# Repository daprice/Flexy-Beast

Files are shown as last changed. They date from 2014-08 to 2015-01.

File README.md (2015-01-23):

Flexy Beast
===========

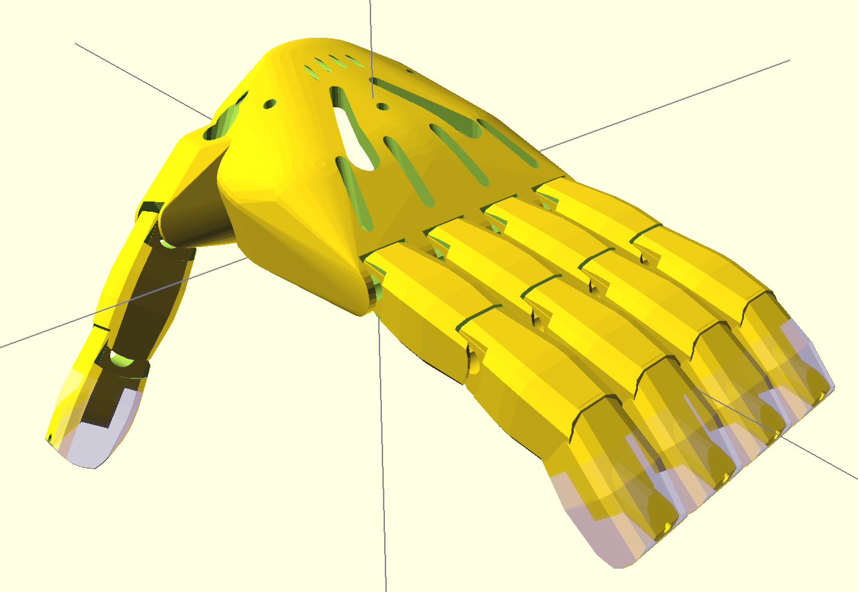
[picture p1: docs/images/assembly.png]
Screenshot of Flexy Beast hand in OpenSCAD


The Flexy Beast is a wrist-powered prosthetic hand for the [e-NABLE Project](http://enablingthefuture.org). This is a mashup of the [Parametric Cyborg Beast](http://www.thingiverse.com/thing:320173) by MakerBlock and the [Flexy Hand](http://www.thingiverse.com/thing:380665) by Steve Wood/Gyrobot. Like the Flexy-Hand, the Flexy Beast uses flexible joints to replace the Chicago screws and elastics used on previous e-NABLE designs. This makes the hand lightweight, less expensive, better looking, more adaptable for smaller sizes, and easier to assemble and use.

I recommend using Filaflex (get these from the original [Flexy Hand](http://www.thingiverse.com/thing:380665)) or [molded silicone flex joints](https://github.com/daprice/Flexy-Joint/tree/FlexyBeast) for this design. See the [Flexy Joint wiki](https://github.com/daprice/Flexy-Joint/wiki) for information about materials to use and the process of making these joints.

### Finger Pads
The Flexy Beast fingers can be made with silicone finger pads for improved grip. These finger pads are designed to be easily removeable and replaceable by hand, but attach firmly enough to stay on during use.
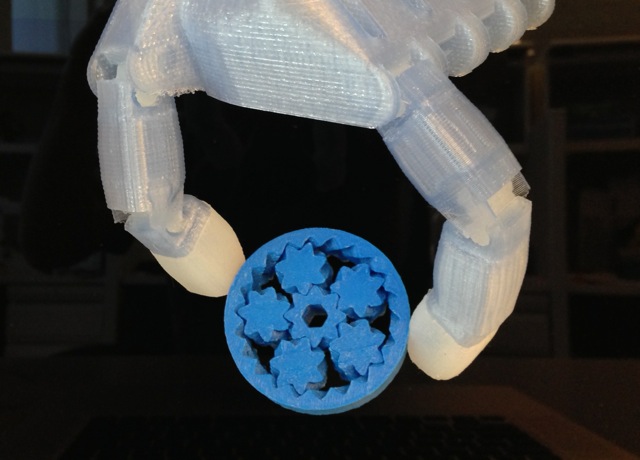
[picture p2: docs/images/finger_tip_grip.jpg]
Fingertips with the ends covered in silicone padding


## Hand Assembly
See the [ThingDoc documentation for the Flexy Beast](http://daprice.github.io/Flexy-Beast) for detailed sizing and assembly instructions.

## Future Improvements
* Flexible joints for gauntlet attachment (this is currently unchanged from the original Cyborg Beast)
* Possible aesthetic options such as text, decorative elements, superhero themes, etc.

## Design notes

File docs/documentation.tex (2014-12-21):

\documentclass[11pt]{article}
\usepackage[latin2]{inputenc}
\usepackage{a4wide}
\usepackage{graphicx}
\usepackage{hyperref}
\hypersetup{colorlinks=true,linkcolor=blue}
\title{Flexy Beast Documentation}
\author{ThingDoc}

\begin{document}

\maketitle
\begin{center}
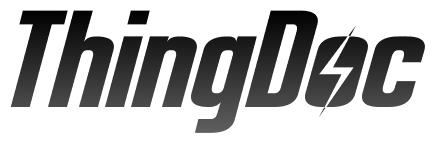
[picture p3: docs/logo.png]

\end{center}
The Flexy Beast is a wrist-powered prosthetic hand for the e-NABLE Project. This is a mashup of the Parametric Cyborg Beast by MakerBlock and the Flexy Hand by Steve Wood/Gyrobot. Like the Flexy-Hand, the Flexy Beast uses flexible joints to replace the Chicago screws and elastics used on previous e-NABLE designs. This makes the hand lightweight, less expensive, better looking, more adaptable for smaller sizes, and easier to assemble and use.

\newpage

\tableofcontents

\newpage

\section{Bill of Materials}
List of things you need to build the machine divided by categories.

\subsection{Prerequisites!}
\begin{itemize}
\item 1x \hyperlink{thing_config\_file}{Configuration File}
\end{itemize}

\subsection{Flexible}
\begin{itemize}
\item 10x \hyperlink{thing_flexy\_joint}{Flexy Joint}
\end{itemize}

\subsection{Other}
\begin{itemize}
\item 5x \hyperlink{thing_string}{String}
\end{itemize}

\subsection{Printed}
\begin{itemize}
\item 1x \hyperlink{thing_thumb\_tip}{Thumb Tip}
\item 1x \hyperlink{thing_index\_base}{Index Finger Base}
\item 1x \hyperlink{thing_pinky\_tip}{Pinky Finger Tip}
\item 5x \hyperlink{thing_finger\_tip\_mold}{Finger Tip Mold}
\item 1x \hyperlink{thing_pinky\_base}{Pinky Finger Base}
\item 1x \hyperlink{thing_ring\_tip}{Ring Finger Tip}
\item 1x \hyperlink{thing_index\_tip}{Index Finger Tip}
\item 1x \hyperlink{thing_palm}{Palm}
\item 1x \hyperlink{thing_ring\_base}{Ring Finger Base}
\item 1x \hyperlink{thing_thumb\_base}{Thumb Base}
\item 1x \hyperlink{thing_middle\_tip}{Middle Finger Tip}
\item 1x \hyperlink{thing_middle\_base}{Middle Finger Base}
\end{itemize}

\newpage

\section{Things Overview}
List of things and their descriptions.

\hypertarget{thing_middle\_finger\_assembly}{\subsection{Assembled Middle Finger}}

\hypertarget{thing_ring\_finger\_assembly}{\subsection{Assembled Ring Finger}}

\hypertarget{thing_palm}{\subsection{Palm}}
Palm - rendered from parts/palm.scad
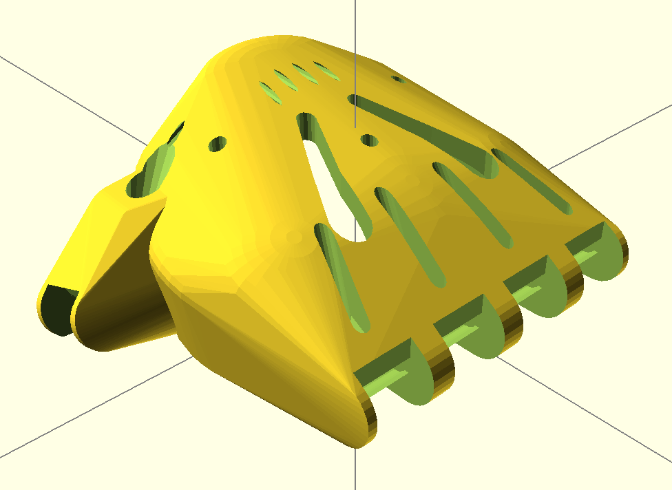
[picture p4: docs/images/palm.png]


\hypertarget{thing_ring\_base}{\subsection{Ring Finger Base}}
Proximal phalanx for ring finger - rendered from parts/finger_ring_base.scad

\hypertarget{thing_finger\_tip\_mold}{\subsection{Finger Tip Mold}}
Mold for casting silicone finger tip grip - rendered from parts/finger_tip_mold.scad


\hypertarget{thing_middle\_tip}{\subsection{Middle Finger Tip}}
Distal phalanx of middle finger - rendered from parts/finger_middle_tip.scad

\hypertarget{thing_ring\_tip}{\subsection{Ring Finger Tip}}
Distal phalanx of ring finger - rendered from parts/finger_ring_tip.scad

\hypertarget{thing_flexy\_joint}{\subsection{Flexy Joint}}
Flex joint - can be molded in silicone or printed in Filaflex. The Configuration File instructions will help you find a good size for these.

\hypertarget{thing_thumb\_base}{\subsection{Thumb Base}}
Proximal phalanx for thumb - rendered from parts/thumb_base.scad

\hypertarget{thing_pinky\_finger\_assembly}{\subsection{Assembled Pinky Finger}}

\hypertarget{thing_config\_file}{\subsection{Configuration File}}
Configuration settings for Flexy Beast, required to generate correctly sized STLs of the printed parts. See the Configuration File Assembly instructions to set this up.

\hypertarget{thing_string}{\subsection{String}}
Just some string

\hypertarget{thing_pinky\_tip}{\subsection{Pinky Finger Tip}}
Distal phalanx of pinky finger - rendered from parts/finger_pinky_tip.scad

\hypertarget{thing_middle\_base}{\subsection{Middle Finger Base}}
Proximal phalanx for middle finger - rendered from parts/finger_middle_base.scad

\hypertarget{thing_thumb\_tip\_grip}{\subsection{Grippy Thumb Tip}}
Molded silicone grippy thumb tip

\hypertarget{thing_index\_base}{\subsection{Index Finger Base}}
Proximal phalanx for index finger - rendered from parts/finger_index_base.scad

\hypertarget{thing_finger\_tip\_grip}{\subsection{Grippy Finger Tip}}
The Flexy Beast fingers can be made with silicone finger pads for improved grip. These finger pads are designed to be easily removeable and replaceable by hand, but attach firmly enough to stay on during use. Dragon Skin 10 silicone produces very soft and grippy pads; Dragon Skin 30 is tougher.


\hypertarget{thing_thumb\_tip}{\subsection{Thumb Tip}}
Distal phalanx of thumb - rendered from parts/thumb_tip.scad


\hypertarget{thing_thumb\_assembly}{\subsection{Assembled Thumb}}

\hypertarget{thing_index\_tip}{\subsection{Index Finger Tip}}
Distal phalanx of index finger - rendered from parts/finger_index_tip.scad

\hypertarget{thing_index\_finger\_assembly}{\subsection{Assembled Index Finger}}

\hypertarget{thing_pinky\_base}{\subsection{Pinky Finger Base}}
Proximal phalanx for pinky finger - rendered from parts/finger_pinky_base.scad

\newpage

\section{Assembly Instructions}

\subsection{Assemble Grippy Finger Tip}
Things needed:
\begin{itemize}
\item 1x \hyperlink{thing_finger\_tip\_mold}{Finger Tip Mold}
\end{itemize}
Steps:
\begin{enumerate}
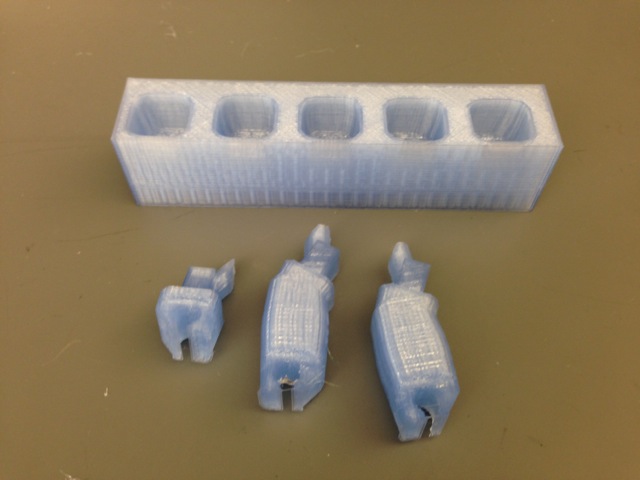
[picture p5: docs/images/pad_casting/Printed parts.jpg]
\item Print the finger tip and mold.\\ 
\item Insert the string through the fingertip and tie off the end prior to molding (not shown in all photos here).\\ 
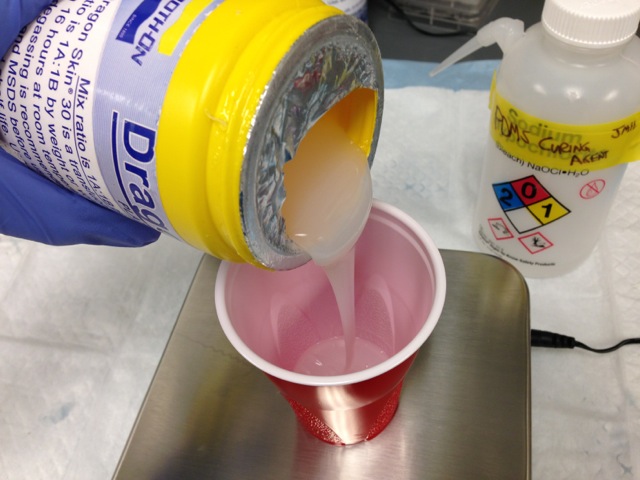
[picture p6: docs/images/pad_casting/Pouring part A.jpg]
\item Mix silicone according to the instructions from the supplier. Wear gloves and follow the supplier's safety instructions while working with liquid silicone.\\ 
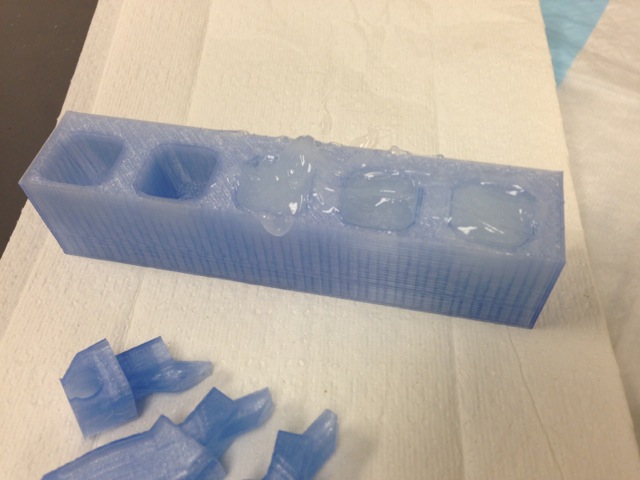
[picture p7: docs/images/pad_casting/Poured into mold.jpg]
\item Pour the liquid silicone to mostly fill the fingertip mold.\\ 
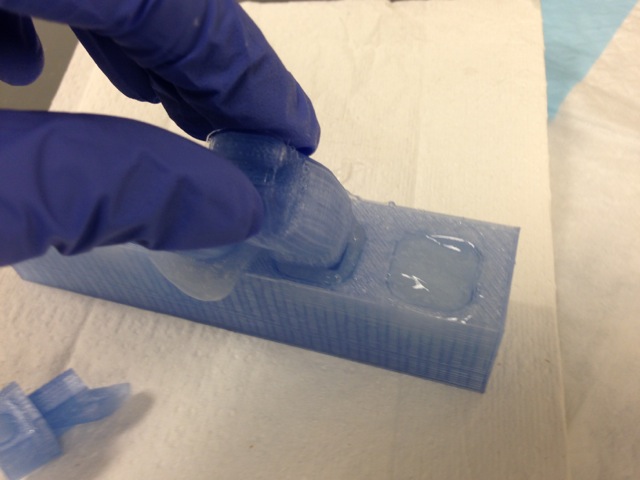
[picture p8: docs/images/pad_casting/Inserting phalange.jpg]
\item Insert the printed fingertip piece into the filled mold.\\ 
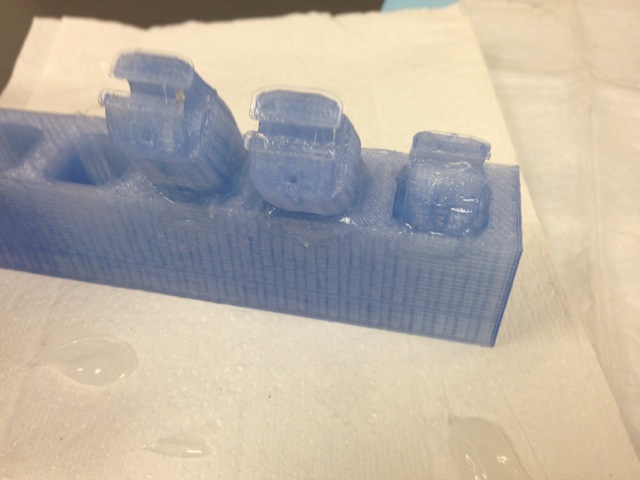
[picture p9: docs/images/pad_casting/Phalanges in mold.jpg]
\item Remove any excess silicone. If necessary, use tape to hold the phalange in place.\\ 
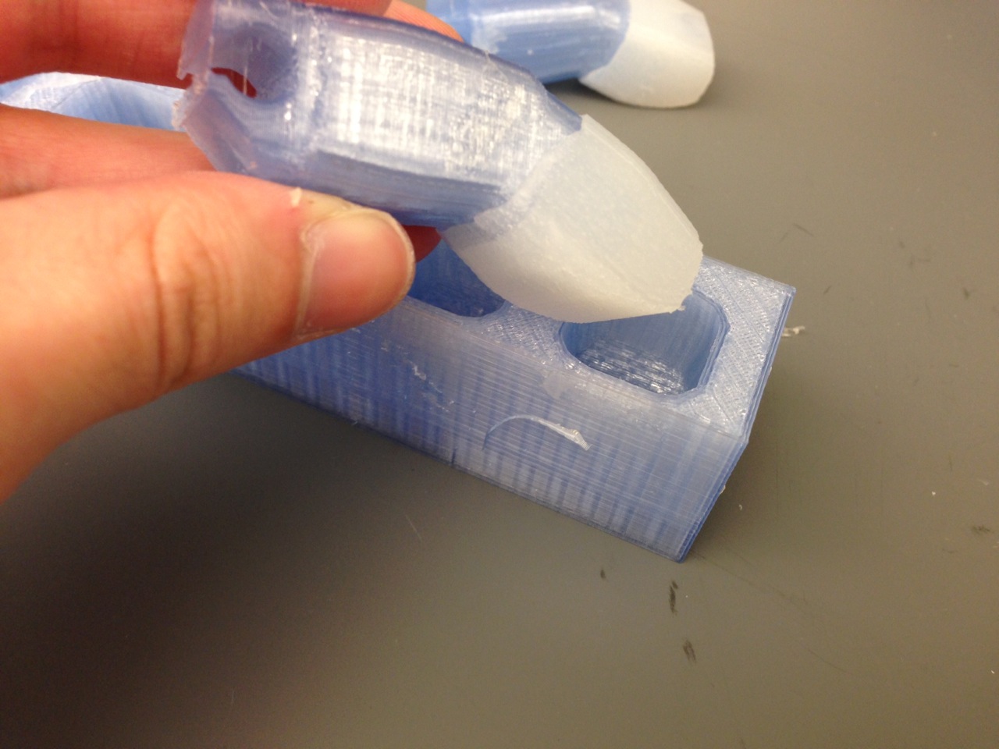
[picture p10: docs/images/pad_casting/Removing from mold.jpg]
\item When the silicone is cured, remove the fingertip and silicone pad from the mold. The pad may stay on the fingertip or it may need to be removed separately.\\ 
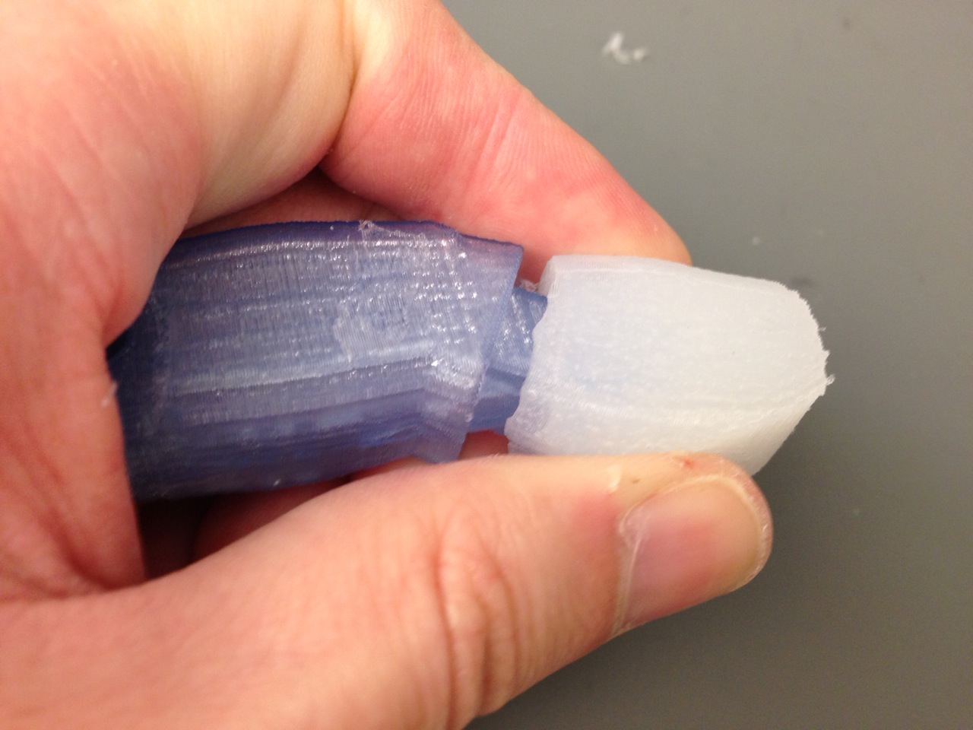
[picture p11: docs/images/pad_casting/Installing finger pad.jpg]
\item If the pad came off the fingertip during demolding, it can be reattached by pushing it over the end of the fingertip.\\ 
\item If necessary, use an x-acto knife to trim off excess silicone so that the edges of the pad are flush with the edges of the fingertip.
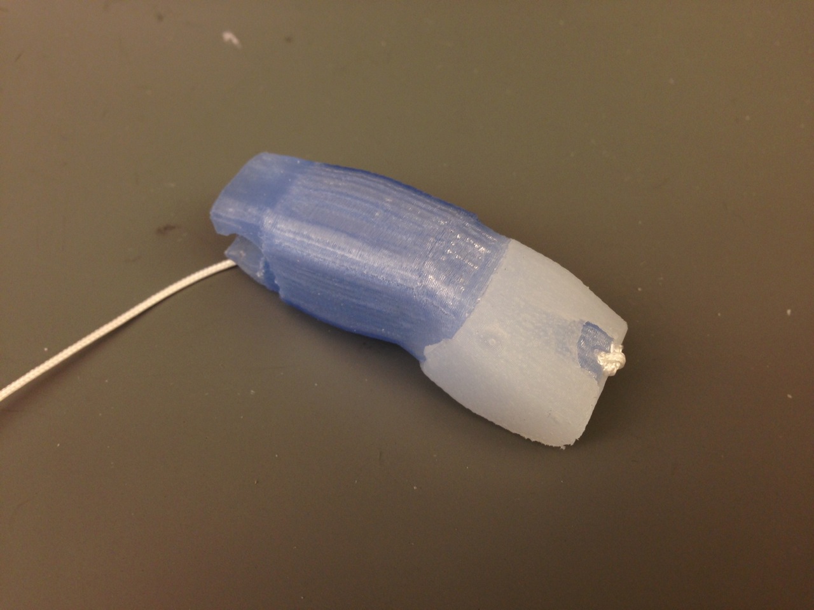
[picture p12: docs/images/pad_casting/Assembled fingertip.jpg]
\item The fingertip pads are finished. Continue installing them onto the hand.\\ 
\end{enumerate}

\subsection{Assemble Grippy Finger Tip}
Things needed:
\begin{itemize}
\item 1x \hyperlink{thing_finger\_tip\_mold}{Finger Tip Mold}
\end{itemize}
Steps:
\begin{enumerate}
\item Print the finger tip and mold.\\ 
\item Insert the string through the fingertip and tie off the end prior to molding (not shown in all photos here).\\ 
\item Mix silicone according to the instructions from the supplier. Wear gloves and follow the supplier's safety instructions while working with liquid silicone.\\ 
\item Pour the liquid silicone to mostly fill the fingertip mold.\\ 
\item Insert the printed fingertip piece into the filled mold.\\ 
\item Remove any excess silicone. If necessary, use tape to hold the phalange in place.\\ 
\item When the silicone is cured, remove the fingertip and silicone pad from the mold. The pad may stay on the fingertip or it may need to be removed separately.\\ 
\item If the pad came off the fingertip during demolding, it can be reattached by pushing it over the end of the fingertip.\\ 
\item If necessary, use an x-acto knife to trim off excess silicone so that the edges of the pad are flush with the edges of the fingertip.
\item The fingertip pads are finished. Continue installing them onto the hand.\\ 
\end{enumerate}

\subsection{Assemble Configuration File}Steps:
\begin{enumerate}
\item Open config.scad in your favorite text editor.
\item As per the normal Cyborg Beast instructions, measure the width of the knuckles in the non-affected hand and convert to millimeters.
\item Add 5 to that result and then divide by 55.
\item Replace the x-, y-, and zScaleFactor variables in config.scad with that number.
\item If desired, adjust the proportions of the hand by changing those variables individually. xScaleFactor controls the width of the hand, yScaleFactor controls the length, and zScaleFactor controls the height.
\item Open assembly.scad in OpenSCAD to check that the flexy joint holes are not too large for the hand (should only be necessary for small children). If necessary, reduce the jointDia and jointThick variables. jointDia=5 and jointThick=2 is a good amount for smaller hands.
\item Set the fingerPads variable to true or false depending on whether you want to cast silicone finger pads for improved grip.
\item Open palm.scad, finger\_base.scad, finger\_tip.scad, and thumb\_tip.scad in OpenSCAD, render each part (F6), and export as STL, then print. Suggested print settings are 0.2mm or smaller layer height, 3 perimeters, and 25\% rectilinear or hexagonal infill.
\end{enumerate}

\subsection{Assemble Grippy Finger Tip}
Things needed:
\begin{itemize}
\item 1x \hyperlink{thing_finger\_tip\_mold}{Finger Tip Mold}
\end{itemize}
Steps:
\begin{enumerate}
\item Print the finger tip and mold.\\ 
\item Insert the string through the fingertip and tie off the end prior to molding (not shown in all photos here).\\ 
\item Mix silicone according to the instructions from the supplier. Wear gloves and follow the supplier's safety instructions while working with liquid silicone.\\ 
\item Pour the liquid silicone to mostly fill the fingertip mold.\\ 
\item Insert the printed fingertip piece into the filled mold.\\ 
\item Remove any excess silicone. If necessary, use tape to hold the phalange in place.\\ 
\item When the silicone is cured, remove the fingertip and silicone pad from the mold. The pad may stay on the fingertip or it may need to be removed separately.\\ 
\item If the pad came off the fingertip during demolding, it can be reattached by pushing it over the end of the fingertip.\\ 
\item If necessary, use an x-acto knife to trim off excess silicone so that the edges of the pad are flush with the edges of the fingertip.
\item The fingertip pads are finished. Continue installing them onto the hand.\\ 
\end{enumerate}

\subsection{Assemble Grippy Finger Tip}
Things needed:
\begin{itemize}
\item 1x \hyperlink{thing_finger\_tip\_mold}{Finger Tip Mold}
\end{itemize}
Steps:
\begin{enumerate}
\item Print the finger tip and mold.\\ 
\item Insert the string through the fingertip and tie off the end prior to molding (not shown in all photos here).\\ 
\item Mix silicone according to the instructions from the supplier. Wear gloves and follow the supplier's safety instructions while working with liquid silicone.\\ 
\item Pour the liquid silicone to mostly fill the fingertip mold.\\ 
\item Insert the printed fingertip piece into the filled mold.\\ 
\item Remove any excess silicone. If necessary, use tape to hold the phalange in place.\\ 
\item When the silicone is cured, remove the fingertip and silicone pad from the mold. The pad may stay on the fingertip or it may need to be removed separately.\\ 
\item If the pad came off the fingertip during demolding, it can be reattached by pushing it over the end of the fingertip.\\ 
\item If necessary, use an x-acto knife to trim off excess silicone so that the edges of the pad are flush with the edges of the fingertip.
\item The fingertip pads are finished. Continue installing them onto the hand.\\ 
\end{enumerate}

\subsection{Assemble Flexy Beast}
Things needed:
\begin{itemize}
\item 1x \hyperlink{thing_middle\_finger\_assembly}{Assembled Middle Finger}
\item 1x \hyperlink{thing_pinky\_finger\_assembly}{Assembled Pinky Finger}
\item 1x \hyperlink{thing_config\_file}{Configuration File}
\item 1x \hyperlink{thing_thumb\_assembly}{Assembled Thumb}
\item 1x \hyperlink{thing_ring\_finger\_assembly}{Assembled Ring Finger}
\item 1x \hyperlink{thing_palm}{Palm}
\item 1x \hyperlink{thing_index\_finger\_assembly}{Assembled Index Finger}
\end{itemize}
Steps:
\begin{enumerate}
\item Print the palm, thumb base, thumb tip, and four each of the finger base and tip. These can be scaled as needed in each dimension using the x-, y-, and zScaleFactor variables in the OpenSCAD code.
\item Insert a string through each fingertip (the hole may need to be drilled slightly to deburr) and tie it off on the end.\\ 
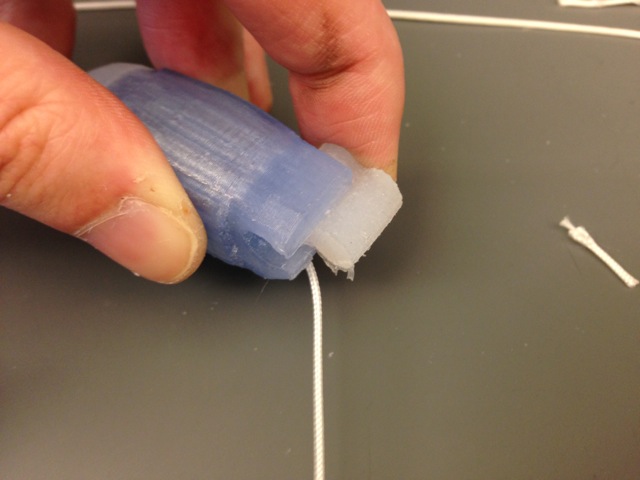
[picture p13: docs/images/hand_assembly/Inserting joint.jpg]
\item After making the 3D printed parts and flexible joints, slide a flex joint into the proximal end of each finger.\\ 
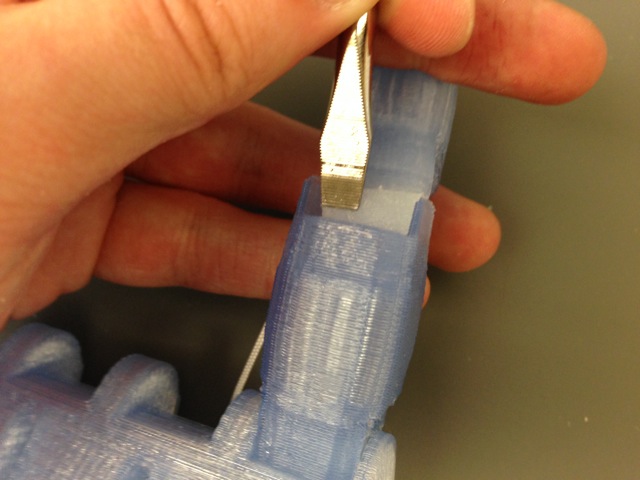
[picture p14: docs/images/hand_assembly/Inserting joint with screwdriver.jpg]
\item Use a flat screwdriver or other thin, flat tool to insert the other end of the joint into the corresponding slot on the next inner segment.\\ 
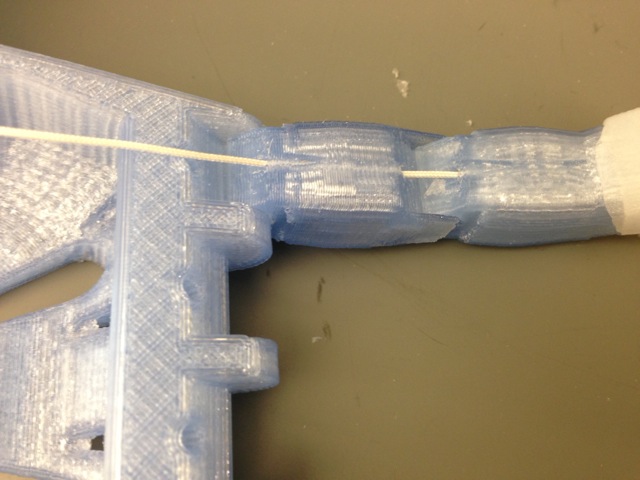
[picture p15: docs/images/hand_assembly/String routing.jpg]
\item Route the string through all the finger segments.\\ 
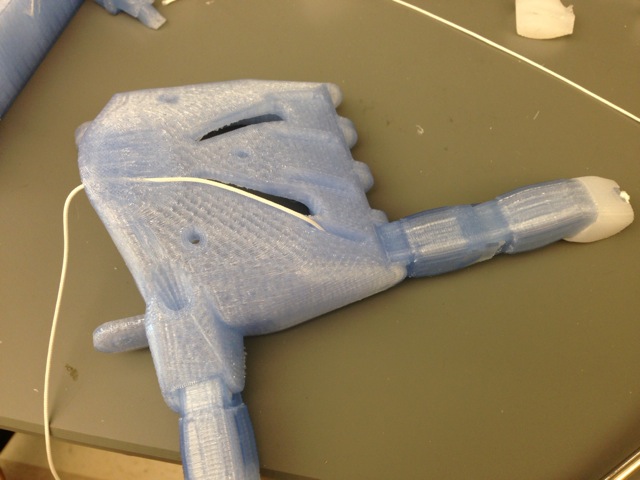
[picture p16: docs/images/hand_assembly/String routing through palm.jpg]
\item Route the string through the palm.\\ 
\end{enumerate}

\newpage

\end{document}

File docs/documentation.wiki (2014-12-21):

== Bill of Materials ==

=== Prerequisites! ===
{| class="wikitable sortable" border="1"
|-
! scope="col" | Quantity
! scope="col" | Description
! scope="col" | Type
! scope="col" class="unsortable" | Comments
! scope="col" class="unsortable" | Diagram
|-
| 1 || Configuration File ||  ||  ||
|}

=== Flexible ===
{| class="wikitable sortable" border="1"
|-
! scope="col" | Quantity
! scope="col" | Description
! scope="col" | Type
! scope="col" class="unsortable" | Comments
! scope="col" class="unsortable" | Diagram
|-
| 10 || Flexy Joint ||  ||  ||
|}

=== Other ===
{| class="wikitable sortable" border="1"
|-
! scope="col" | Quantity
! scope="col" | Description
! scope="col" | Type
! scope="col" class="unsortable" | Comments
! scope="col" class="unsortable" | Diagram
|-
| 5 || String ||  ||  ||
|}

=== Printed ===
{| class="wikitable sortable" border="1"
|-
! scope="col" | Quantity
! scope="col" | Description
! scope="col" | Type
! scope="col" class="unsortable" | Comments
! scope="col" class="unsortable" | Diagram
|-
| 1 || Thumb Tip ||  ||  || 50px
|-
| 1 || Index Finger Base ||  ||  ||
|-
| 1 || Pinky Finger Tip ||  ||  ||
|-
| 5 || Finger Tip Mold ||  ||  || 50px
|-
| 1 || Pinky Finger Base ||  ||  ||
|-
| 1 || Ring Finger Tip ||  ||  ||
|-
| 1 || Index Finger Tip ||  ||  ||
|-
| 1 || Palm ||  ||  || 50px
|-
| 1 || Ring Finger Base ||  ||  ||
|-
| 1 || Thumb Base ||  ||  ||
|-
| 1 || Middle Finger Tip ||  ||  ||
|-
| 1 || Middle Finger Base ||  ||  ||
|}

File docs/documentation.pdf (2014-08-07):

## Flexy Beast Documentation

ThingDoc

August 7, 2014

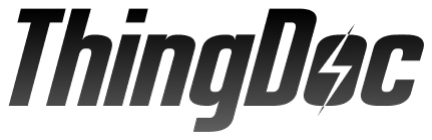
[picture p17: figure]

The Flexy Beast is a wrist-powered prosthetic hand for the e-NABLE Project. This is a mashup of the Parametric Cyborg Beast by MakerBlock and the Flexy Hand by Steve Wood/Gyrobot. Like the Flexy-Hand, the Flexy Beast uses flexible joints to replace the Chicago screws and elastics used on previous e-NABLE designs. This makes the hand lightweight, less expensive, better looking, more adaptable for smaller sizes, and easier to assemble and use.

## Contents

1 Bill of Materials | 3
1.1 Prerequisites! | | 3
1.2 Flexible | | 3
1.3 Other | | 3
1.4 Printed | | 3
2 Things Overview | 4
2.1 Grippy Thumb Tip | | 4
2.2 Configuration File | | 4
2.3 String | | 4
2.4 Grippy Finger Tip | | 4
2.5 Finger Tip | | 4
2.6 Finger Base | | 5
2.7 Thumb Tip | | 5
2.8 Assembled Thumb | | 5
2.9 Palm | | 5
2.10 Flexy Joint | | 5
2.11 Assembled Finger | | 6
2.12 Finger Tip Mold | | 6
3 Assembly Instructions | 7
3.1 Assemble Configuration File | | 7
3.2 Assemble Grippy Finger Tip | | 7
3.3 Assemble Flexy Beast | | 9

## 1 Bill of Materials

List of things you need to build the machine divided by categories.

### 1.1 Prerequisites!

- 1x Configuration File

### 1.2 Flexible

- 10x Flexy Joint

### 1.3 Other

- 5x String

### 1.4 Printed

- 4x Finger Tip
- 5x Finger Tip Mold
- 1x Palm
- 5x Finger Base
- 1x Thumb Tip

## 2 Things Overview

List of things and their descriptions.

### 2.1 Grippy Thumb Tip

Molded silicone grippy thumb tip

### 2.2 Configuration File

Configuration settings for Flexy Beast, required to generate correctly sized STLs of the printed parts. See the Configuration File Assembly instructions to set this up.

### 2.3 String

Just some string

### 2.4 Grippy Finger Tip

The Flexy Beast fingers can be made with silicone finger pads for improved grip. These finger pads are designed to be easily removeable and replaceable by hand, but attach firmly enough to stay on during use. Dragon Skin 10 silicone produces very soft and grippy pads; Dragon

Skin 30 is tougher.


### 2.5 Finger Tip

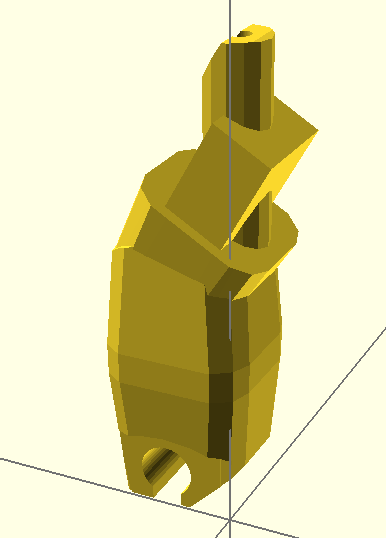
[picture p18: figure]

Distal phalanx of fingers - rendered from parts/finger tip.scad

### 2.6 Finger Base

Proximal phalanx for all digits (fingers and thumb) - rendered from parts/finger base.scad

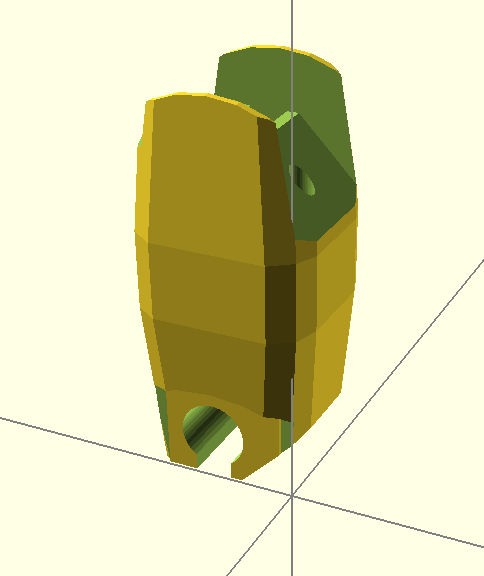
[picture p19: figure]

### 2.7 Thumb Tip

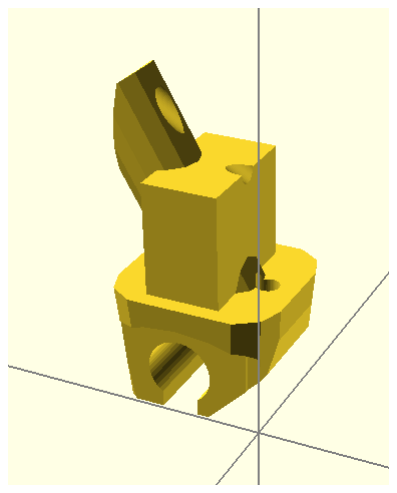
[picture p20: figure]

Distal phalanx of thumb - rendered from parts/thumb tip.scad

### 2.8 Assembled Thumb

### 2.9 Palm

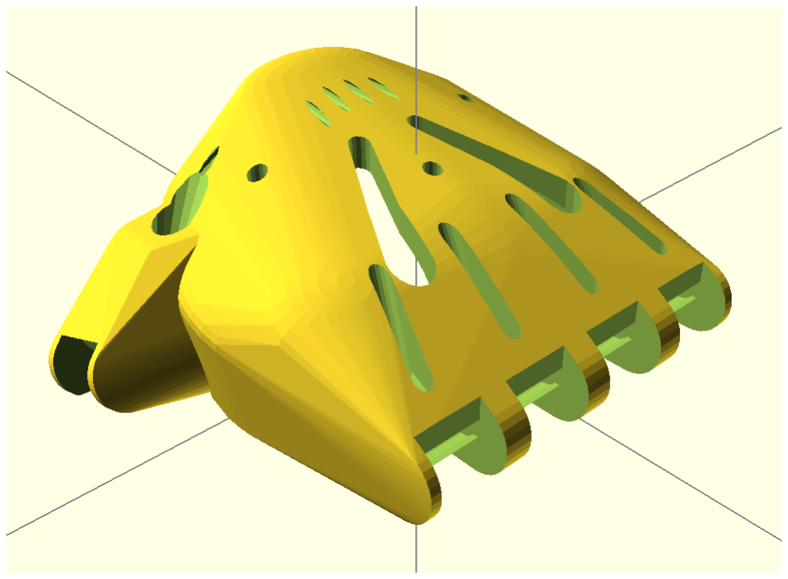
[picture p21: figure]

Palm - rendered from parts/palm.scad

### 2.10 Flexy Joint

Flex joint - can be molded in silicone or printed in Filaflex. The Configuration File instructions will help you find a good size for these.

### 2.11 Assembled Finger

### 2.12 Finger Tip Mold

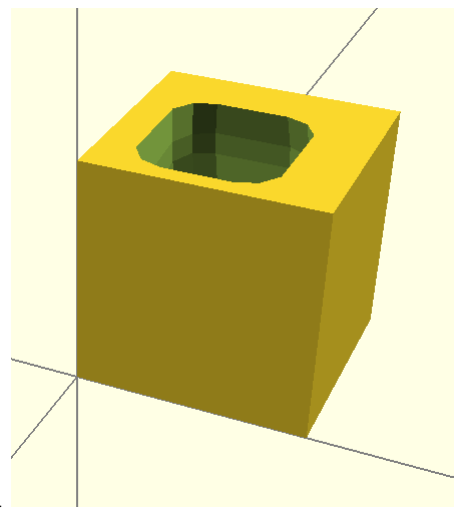
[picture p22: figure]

Mold for casting silicone finger tip grip - rendered from parts/finger tip mold.scad

## 3 Assembly Instructions

### 3.1 Assemble Configuration File

Steps:

1. Open config.scad in your favorite text editor.
2. As per the normal Cyborg Beast instructions, measure the width of the knuckles in the non-affected hand and convert to millimeters.
3. Add 5 to that result and then divide by 55.
4. Replace the x-, y-, and zScaleFactor variables in config.scad with that number.
5. If desired, adjust the proportions of the hand by changing those variables individually. xScaleFactor controls the width of the hand, yScaleFactor controls the length, and zScaleFactor controls the height.
6. Open assembly.scad in OpenSCAD to check that the flexy joint holes are not too large for the hand (should only be necessary for small children). If necessary, reduce the jointDia and jointThick variables. jointDia=5 and jointThick=2 is a good amount for smaller hands.
7. Set the fingerPads variable to true or false depending on whether you want to cast silicone finger pads for improved grip.
8. In palm.scad, finger base.scad, finger tip.scad, and thumb tip.scad, uncomment the first line that renders the part.
9. Render each part (F6) and export as STL, then print.

### 3.2 Assemble Grippy Finger Tip

Things needed:

- 1x Finger Tip
- 1x Finger Tip Mold

Steps:


1. Print the finger tip and mold.

parts.jpg

2. Insert the string through the fingertip and tie off the end prior to molding (not shown in all photos here).

with string.jpg

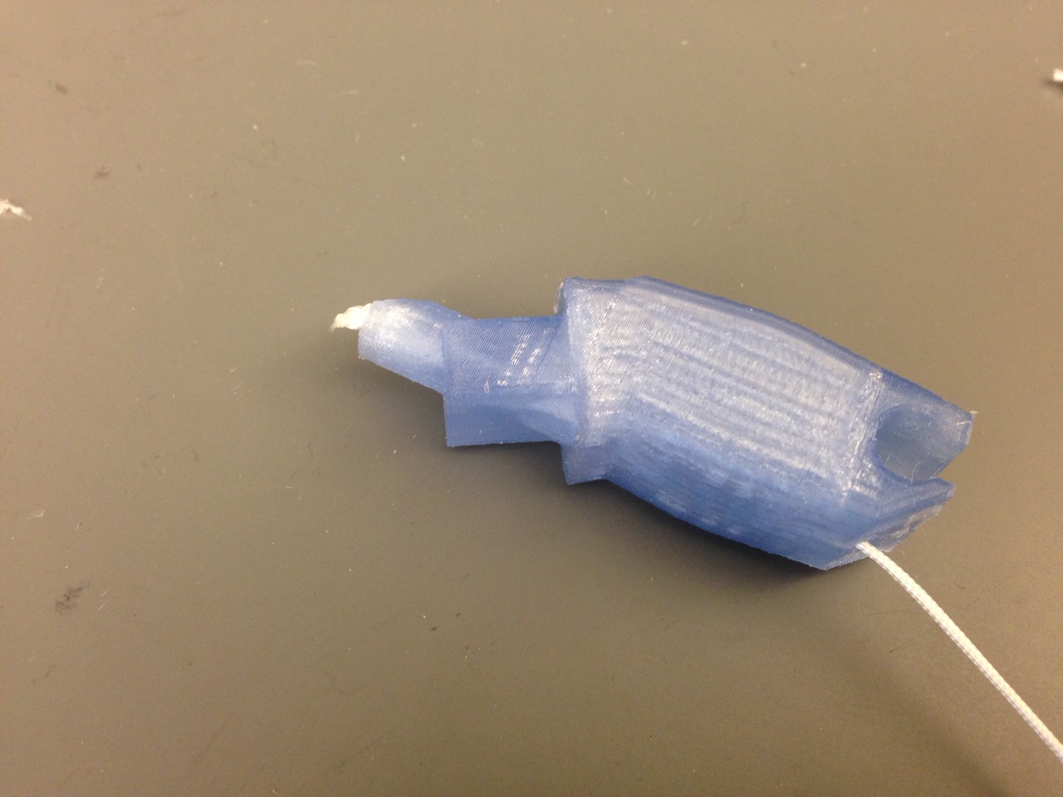
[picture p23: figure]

3. Mix silicone according to the instructions from the supplier. Wear gloves and follow the supplier’s safety instructions while working with liquid silicone.

part A.jpg


4. Pour the liquid silicone to mostly fill the fingertip mold.

into mold.jpg


5. Insert the printed fingertip piece into the filled mold.

phalange.jpg


6. Remove any excess silicone. If necessary, use tape to hold the phalange in place.

in mold.jpg


7. When the silicone is cured, remove the fingertip and silicone pad from the mold. The pad may stay on the fingertip or it may need to be removed separately.

from mold.jpg


8. If the pad came off the fingertip during demolding, it can be reattached by pushing it over the end of the fingertip.

finger pad.jpg


9. If necessary, use an x-acto knife to trim off excess silicone so that the edges of the pad are flush with the edges of the fingertip.
10. The fingertip pads are finished. Continue installing them onto the hand.

fingertip.jpg


### 3.3 Assemble Flexy Beast

Things needed:

- 1x Palm
- 1x Assembled Thumb
- 1x Configuration File
- 4x Assembled Finger

Steps:

1. Print the palm, thumb base, thumb tip, and four each of the finger base and tip. These can be scaled as needed in each dimension using the x-, y-, and zScaleFactor variables in the OpenSCAD code.
2. Insert a string through each fingertip (the hole may need to be drilled slightly to deburr) and tie it off on the end.

with string.jpg

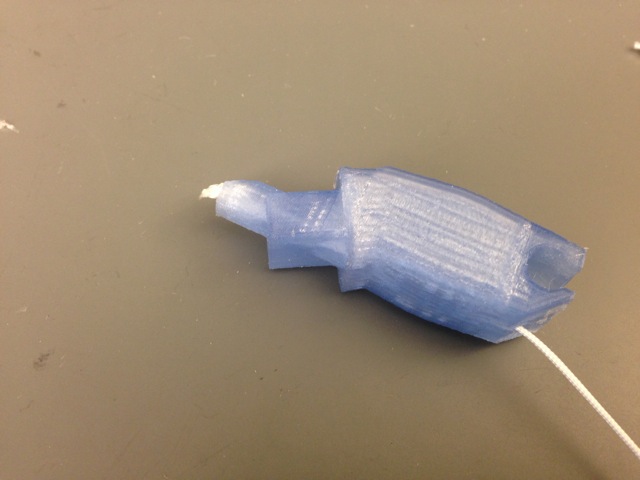
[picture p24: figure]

3. After making the 3D printed parts and flexible joints, slide a flex joint into the proximal end of each finger.

joint.jpg


4. Use a flat screwdriver or other thin, flat tool to insert the other end of the joint into the corresponding slot on the next inner segment.

joint with screwdriver.jpg


5. Route the string through all the finger segments.

routing.jpg


6. Route the string through the palm.

routing through palm.jpg

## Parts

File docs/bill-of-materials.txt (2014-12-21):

Bill of Materials: Flexy Beast
++++++++++++++++++++++++++++++

Prerequisites!
==============
- 1x Configuration File

Flexible
========
- 10x Flexy Joint

Other
=====
- 5x String

Printed
=======
- 1x Thumb Tip
- 1x Index Finger Base
- 1x Pinky Finger Tip
- 5x Finger Tip Mold
- 1x Pinky Finger Base
- 1x Ring Finger Tip
- 1x Index Finger Tip
- 1x Palm
- 1x Ring Finger Base
- 1x Thumb Base
- 1x Middle Finger Tip
- 1x Middle Finger Base

----
Generated on 2014/12/20 22:11:11 by ThingDoc - http://thingdoc.org/

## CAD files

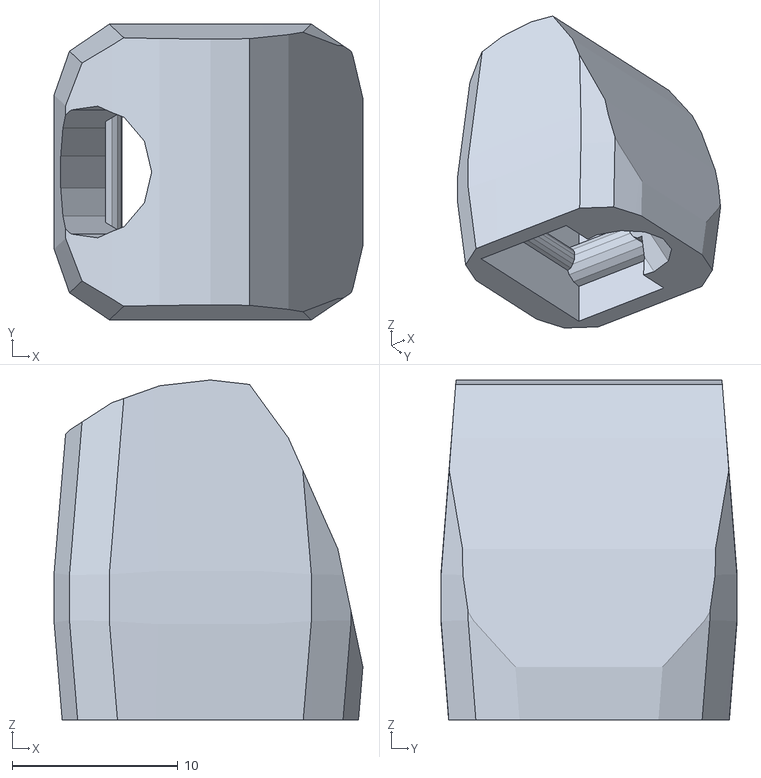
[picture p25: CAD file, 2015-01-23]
stl/finger_tip_flexy_grip.stl
18.6 x 17.8 x 20.5

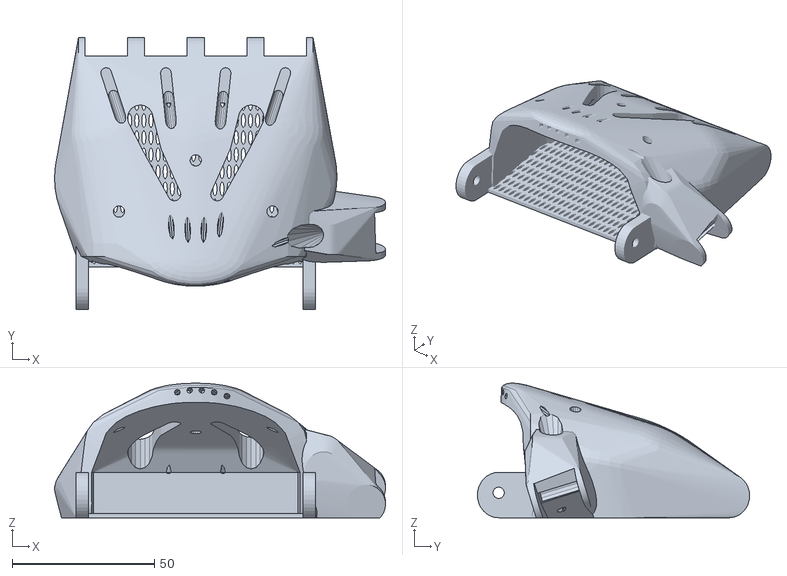
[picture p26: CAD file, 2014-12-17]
stl/palm.stl
116.4 x 95.8 x 47.3

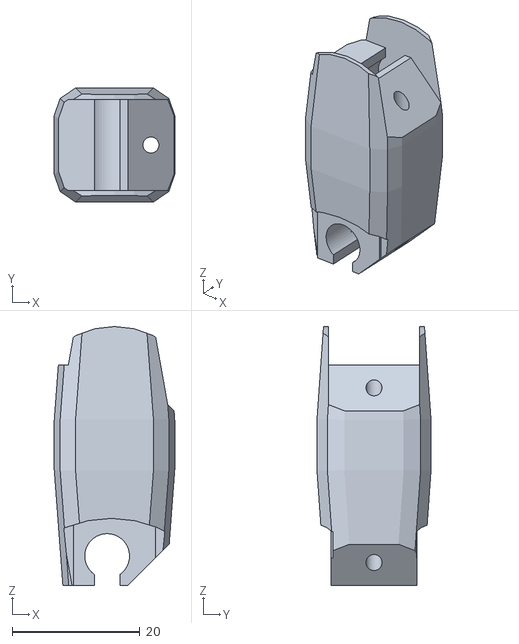
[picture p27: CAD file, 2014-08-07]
stl/finger_base.stl
18.8 x 17.8 x 40.5

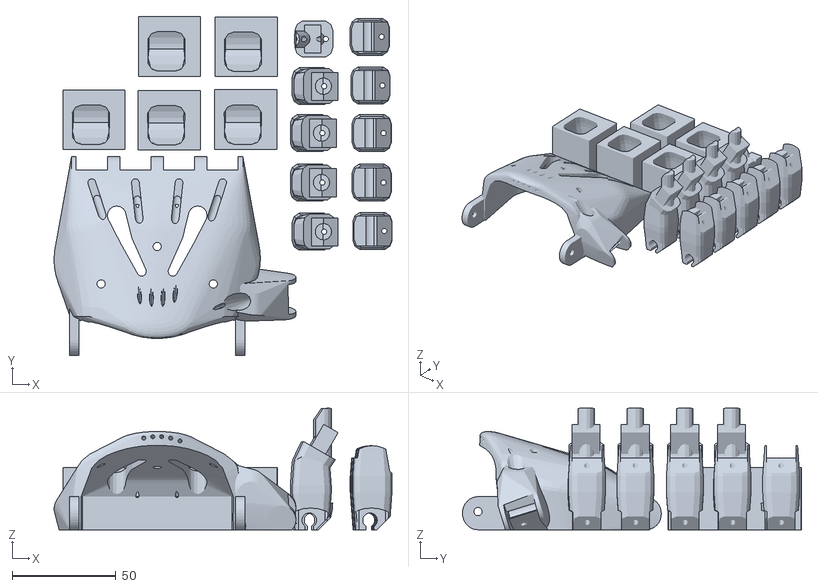
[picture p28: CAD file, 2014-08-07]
stl/single_plate.stl
162.7 x 163.3 x 58.6

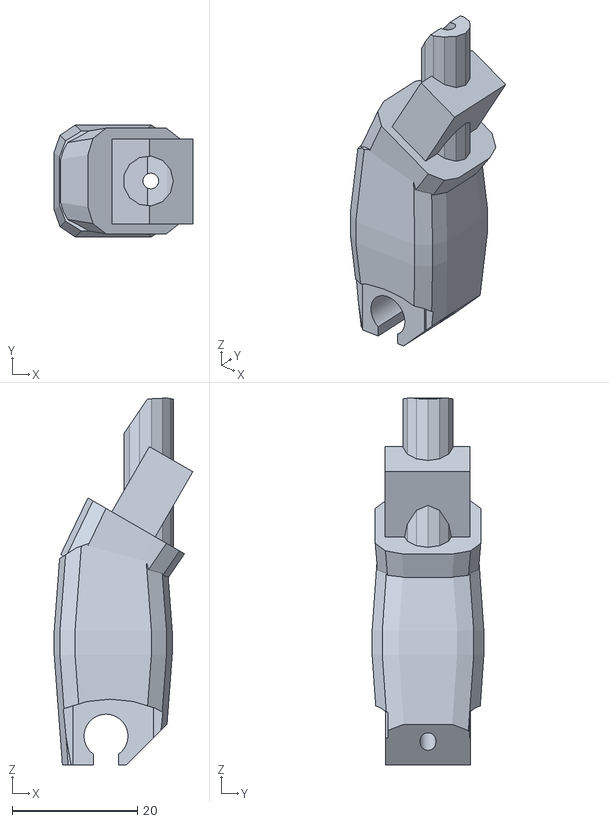
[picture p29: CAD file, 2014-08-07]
stl/finger_tip.stl
22.1 x 17.8 x 58.6

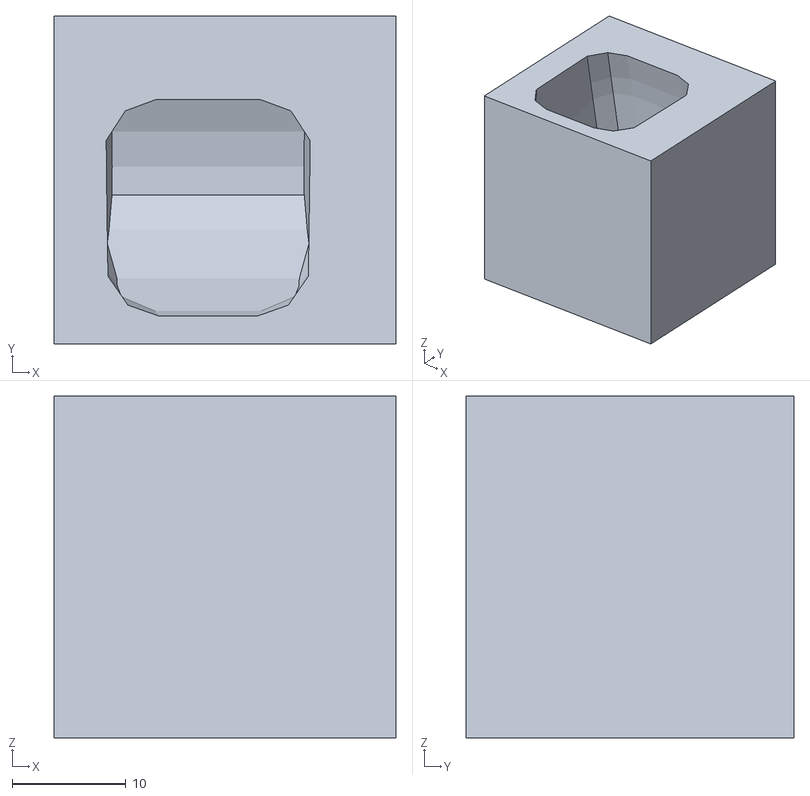
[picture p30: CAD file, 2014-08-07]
stl/finger_tip_mold.stl
30.0 x 28.8 x 30.0

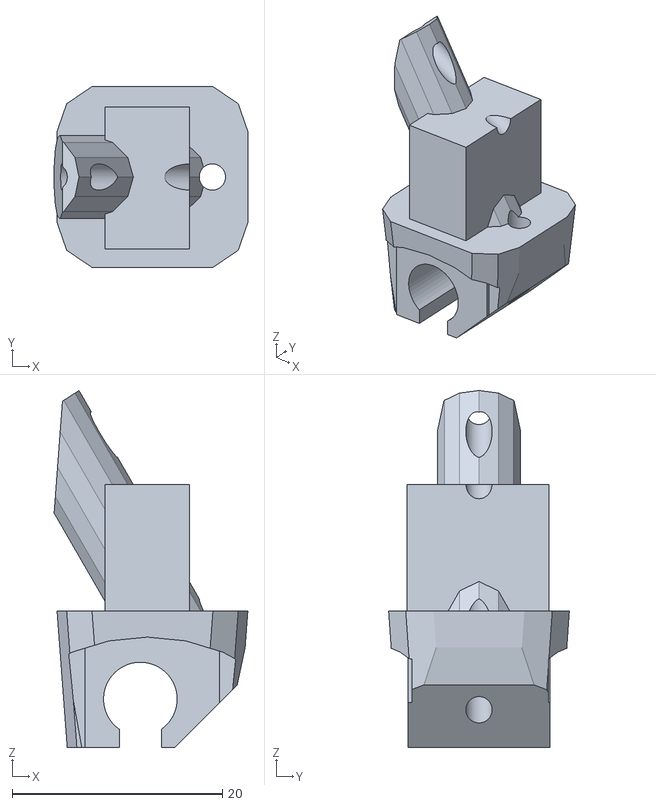
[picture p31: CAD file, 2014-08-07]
stl/thumb_tip.stl
18.4 x 17.2 x 34.0

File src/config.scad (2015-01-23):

/**
 * Configuration settings for Flexy Beast, required to generate correctly sized STLs of the printed parts. See the Configuration File Assembly instructions to set this up.
 * @id config_file
 * @name Configuration File
 * @category Prerequisites!
 * @step Open config.scad in your favorite text editor.
 * @step As per the normal Cyborg Beast instructions, measure the width of the knuckles in the non-affected hand and convert to millimeters.
 * @step Add 5 to that result and then divide by 55.
 * @step Replace the x-, y-, and zScaleFactor variables in config.scad with that number.
 * @step If desired, adjust the proportions of the hand by changing those variables individually. xScaleFactor controls the width of the hand, yScaleFactor controls the length, and zScaleFactor controls the height.
 * @step Open assembly.scad in OpenSCAD to check that the flexy joint holes are not too large for the hand (should only be necessary for small children). If necessary, reduce the jointDia and jointThick variables. jointDia=5 and jointThick=2 is a good amount for smaller hands.
 * @step Set the fingerPads variable to true or false depending on whether you want to cast silicone finger pads for improved grip.
 * @step Open palm.scad, finger_base.scad, finger_tip.scad, and thumb_tip.scad in OpenSCAD, render each part (F6), and export as STL, then print. Suggested print settings are 0.2mm or smaller layer height, 3 perimeters, and 25% rectilinear or hexagonal infill.
 */

knuckleR = 4.85;
knucklePadding = 0.5;
knuckleW = 9.5;
wristH = 10;
palmH = 20;
palmW = 64;
th = 3;
fn = 32;

//flexy joint parameters
jointDia = 7;
jointThick = 4;

//finger settings
fingerPads = true; //whether or not to hollow the finger tips slightly for molding pads
padPositive = false; //if false (default), finger_tip_mold.scad renders a mold to make silicone finger pads; if true, renders a printable flexible finger pad
fingerLength = 1; //multiply the length of all fingers by this amount
thumbProp = 0.8; //proportion of thumb length relative to other fingers (note that the thumb is a segment shorter than the other fingers already)
indexProp = 0.8; //proportion of index finger length relative to other fingers
middleProp = 1; //proportion of middle finger length relative to other fingers
ringProp = 0.8; //proportion of ring finger length relative to other fingers
pinkyProp = 0.7; //proportion of pinky finger length relative to other fingers

//misc settings
thermoform = true; //whether or not to generate a thermoformable mesh for the palm

//desired scale factor for hand based on the standard Cyborg Beast/Robohand sizing guide
xScaleFactor = 1.5; // [1.05:1.60]
yScaleFactor = 1.5; // [1.05:1.60]
zScaleFactor = 1.6; // [1.05:1.60]

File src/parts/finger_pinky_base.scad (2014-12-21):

include <../config.scad>
use <util/finger_base.scad>

rotate([0,-90,0]) fingerbase(length = 20 * pinkyProp * fingerLength);

/**
 * Proximal phalanx for pinky finger - rendered from parts/finger_pinky_base.scad
 * @id pinky_base
 * @name Pinky Finger Base
 * @category Printed
 */

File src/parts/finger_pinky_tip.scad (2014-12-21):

include <../config.scad>
use <util/finger_tip.scad>

rotate([0,-90,0]) fingertip_curved_solid(length = 17*pinkyProp*fingerLength, pad=fingerPads);

/**
 * Distal phalanx of pinky finger - rendered from parts/finger_pinky_tip.scad
 * @id pinky_tip
 * @name Pinky Finger Tip
 * @category Printed
 */

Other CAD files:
cyborgbeast07l.scad
parts/cyborgpalm001.scad
parts/flexyfinger_base.scad
parts/flexyfinger_mid.scad
parts/flexyfinger_tip.scad
parts/flexyfinger_tip_mold.scad
src/assembly.scad
src/parts/finger_base.scad
src/parts/finger_index_base.scad
src/parts/finger_index_tip.scad
src/parts/finger_mid.scad
src/parts/finger_middle_base.scad
src/parts/finger_middle_tip.scad
src/parts/finger_ring_base.scad
src/parts/finger_ring_tip.scad
src/parts/finger_tip.scad
src/parts/finger_tip_mold.scad
src/parts/palm.scad
src/parts/thermoform.scad
src/parts/thumb_base.scad
src/parts/thumb_tip.scad
src/parts/util/finger_base.scad
src/parts/util/finger_mid.scad
src/parts/util/finger_tip.scad
src/parts/util/thermoform.scad

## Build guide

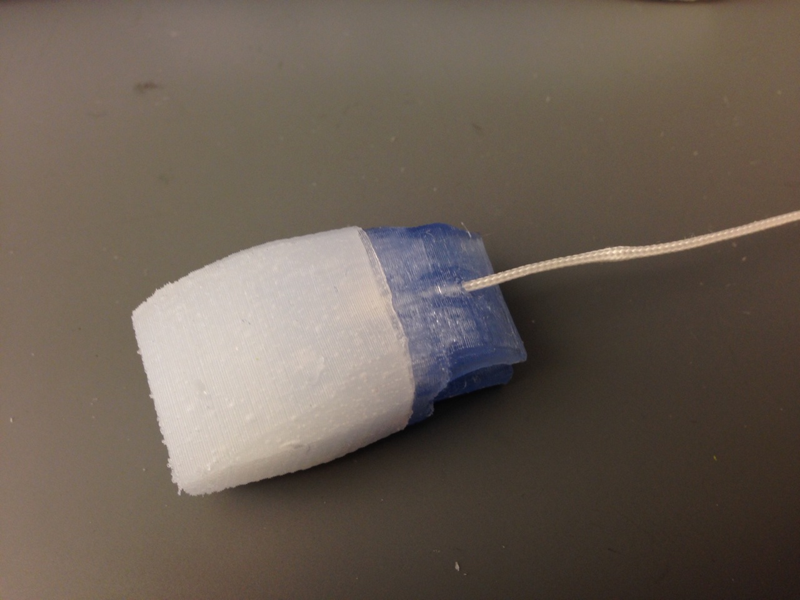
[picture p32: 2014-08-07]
docs/images/pad_casting/Assembled thumb.jpg

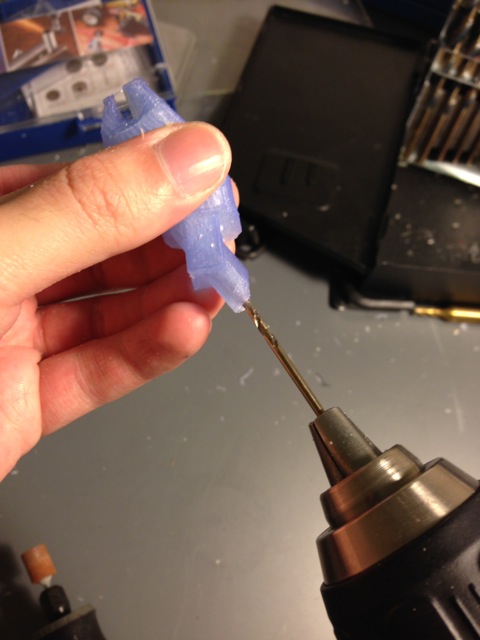
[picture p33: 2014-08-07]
docs/images/hand_assembly/Drilling out fingertip.jpg

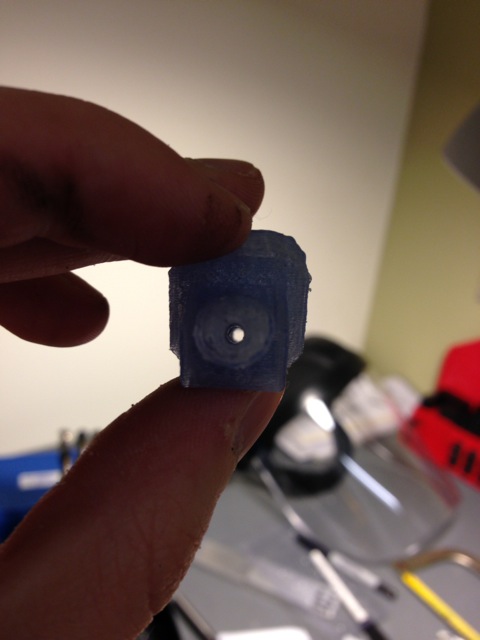
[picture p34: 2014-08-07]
docs/images/hand_assembly/Fingertip hole.jpg

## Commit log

2014-06-24 Initial commit (importing Parametric Cyborg Beast 7.2 by Makerblock from http://www.thingiverse.com/thing:320173 )
    [cyborgbeast07l.scad, cyborgfingermid002.scad, cyborgfingertip002.scad, cyborgpalm001.scad]
2014-06-25 Scale hardware independently of overall hand scale; initial work on adding flex joints
    [cyborgbeast07l.scad, cyborgpalm001.scad]
2014-06-25 Only cut holes for flex joints in the actual knuckle slot, not in between them
    [cyborgpalm001.scad]
2014-06-25 Add flex joint in thumb slot
    [cyborgbeast07l.scad, cyborgpalm001.scad]
2014-06-26 Make finger slots wider; make finger middle piece obey scaleFactor
    [cyborgbeast07l.scad, cyborgfingermid002.scad, cyborgpalm001.scad]
2014-06-27 Adjust finger layout positioning; make fingertips obey scaleFactor parameter
    [cyborgbeast07l.scad, cyborgfingertip002.scad]
2014-06-27 Initial progress in adapting the finger middle to use flex joints
    [cyborgfingermid002.scad]
2014-06-27 Scale each axis of palm separately
    [cyborgbeast07l.scad, cyborgpalm001.scad]
2014-06-27 Do the scaling only on the palm part and not the holes
    [cyborgpalm001.scad]
2014-06-27 Hide fingers for now
    [cyborgbeast07l.scad]
2014-06-29 Modify palm to accomodate finger flexion
    [cyborgpalm001.scad]
2014-06-29 Replace fingers with placeholders for new three-segment versions
    [cyborgbeast07l.scad, cyborgfingermid002.scad, cyborgfingertip002.scad, flexyfinger_base.scad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]
2014-06-30 Create initial design for finger segments; make knuckle joint width a parameter
    [cyborgbeast07l.scad, cyborgpalm001.scad, flexyfinger_base.scad]
2014-06-30 Add parameter for knuckle padding
    [cyborgbeast07l.scad]
2014-07-02 Adjustments to knuckles and finger size
    [cyborgbeast07l.scad, cyborgpalm001.scad, flexyfinger_base.scad]
2014-07-02 Place finger bases in hand layout
    [cyborgbeast07l.scad]
2014-07-02 Make middle sections of fingers; slight refactoring of finger code
    [cyborgbeast07l.scad, flexyfinger_base.scad, flexyfinger_mid.scad]
2014-07-02 Make fingertips; minor adjustments
    [cyborgbeast07l.scad, cyborgpalm001.scad, flexyfinger_tip.scad]
2014-07-02 Add tendon channels in fingers
    [flexyfinger_base.scad, flexyfinger_mid.scad, flexyfinger_tip.scad]
2014-07-03 Fix sizing of finger slots in palm
    [cyborgpalm001.scad]
2014-07-03 Use the larger flex joint everywhere; adjust joint positioning; shorten fingers slightly
    [cyborgbeast07l.scad, flexyfinger_base.scad, flexyfinger_mid.scad, flexyfinger_tip.scad]
2014-07-03 Make sure hole for string goes all the way through the finger parts
    [flexyfinger_base.scad]
2014-07-06 Remove unneeded knuckle blocks; fix knuckle padding on palm; adjust flex joint hole sizes to match latest mold at daprice/Flexy-Joint@093a1c19
    [cyborgbeast07l.scad, cyborgpalm001.scad, flexyfinger_base.scad, flexyfinger_mid.scad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]
2014-07-08 Improve fingertip shape; make the string come out on the top of the fingertip instead of the tip
    [flexyfinger_base.scad, flexyfinger_tip.scad]
2014-07-13 Hollow out fingertips partially to allow for molding in a silicone grippy pad
    [cyborgbeast07l.scad, flexyfinger_tip.scad]
2014-07-13 Add mold for fingertip pad
    [cyborgbeast07l.scad, flexyfinger_tip.scad, flexyfinger_tip_mold.scad]
2014-07-14 Adjust string hole positioning to improve printability of padded fingertip
    [flexyfinger_base.scad]
2014-07-15 Leave more room around string hole so it won't have holes in it when printed
    [flexyfinger_tip.scad]
2014-07-15 Add finger pad details to readme
2014-07-16 Make hopefully better fingertip to cast silicone around
    [flexyfinger_tip.scad]
2014-07-16 Make the padding go further down on the finger
    [flexyfinger_tip.scad]
2014-07-16 Adjust mold for the new finger pads
    [flexyfinger_tip_mold.scad]
2014-07-17 Link to the wiki for instructions on casting finger pads
2014-07-18 Make curved fingertips properly regardless of whether fingerPads is true; make thumb tip respect fingerPads setting
    [cyborgbeast07l.scad, flexyfinger_tip.scad]
2014-07-18 Add OpenSCAD screenshot of assembled hand
2014-08-03 Fix scaling of fingers relative to palm
    [cyborgbeast07l.scad, flexyfinger_base.scad, flexyfinger_mid.scad, flexyfinger_tip.scad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]
2014-08-06 Add finger pads to assembly preview image
2014-08-06 Reorganize and refactor
    [assembly.scad, config.scad, finger_base.scad, finger_mid.scad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]
2014-08-06 Add basic documentation using Thingdoc
    [assembly.scad, finger_base.scad, finger_mid.scad, finger_tip.scad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]
2014-08-07 Flesh out Thingdoc documentation
    [assembly.scad, config.scad, finger_mid.scad, finger_tip.scad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]
2014-08-07 Update Readme to point to the Thingdoc docs and use different image for fingertip pads
2014-08-07 Add hand description in Thingdoc
    [assembly.scad]
2014-08-07 Include references to the files each rendered image is generated from in documentation
    [finger_base.scad, finger_tip.scad, finger_tip_mold.scad, palm.scad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]
2014-08-07 Add STLs of test hand (not sized to fit anyone!)
    [finger_base.stl, finger_tip.stl, finger_tip_mold.stl, palm.stl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]
2014-10-30 Use instead of including the parts of the hand in assembly.scad so the individual part files can be opened and rendered without uncommenting the first line.
    [assembly.scad, config.scad, finger_base.scad, finger_mid.scad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]
2014-10-30 Improve scaling of finger parts at smaller sizes; allow larger flex joints to fit smaller finger parts
    [finger_base.scad, finger_tip.scad]
2014-10-31 Add ridges to improve attachment of silicone fingertip grip to fingers
    [finger_tip.scad]
2014-12-17 Rename scad directory to src to accommodate other source files
    [assembly.scad, config.scad, finger_base.scad, finger_mid.scad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]
2014-12-17 Add optional thermoformable mesh to palm piece – this should provide better force transfer than a velcro pouch/strap
    [config.scad, palm.scad, palm.stl, thermoform.scad]
2014-12-18 adjust thermoform mesh for better flexibility when hot
    [thermoform.scad]
2014-12-18 slight adjustment to thumb angle
    [palm.scad]
2014-12-18 increase thickness/rigidity of palm mesh
    [thermoform.scad]
2014-12-21 Allow each finger to be proportioned differently; assign default finger proportions
    [assembly.scad, config.scad, finger_base.scad, finger_index_base.scad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]
2014-12-21 Fix path to finger_tip.scad in finger_tip_mold.scad
    [assembly.scad, finger_tip_mold.scad]
2015-01-23 Add optional model of finger tip grip that can be printed using flexible filament; add link to readme for printable flex joints (solves #1)
    [config.scad, finger_tip_flexy_grip.stl, finger_tip_mold.scad]
